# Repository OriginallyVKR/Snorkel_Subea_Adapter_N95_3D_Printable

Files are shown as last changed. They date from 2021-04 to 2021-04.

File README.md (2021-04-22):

# Snorkel_Subea_Adapter_N95_3D_Printable
This repo consists of the CAD designs of the adapter to convert a Decathlon - SUBEA snorkelling mask to be used as an N95 Mask for medical personnel. awe designed during the 

# Introduction 

<p>To prevent transmission of the novel SARS-CoV-2 virus among exposed health care workers (HCW), the WHO recommends the use of tight-fitting facepiece respirators such as the FFP2 or N95.1  However, global personal protective equipment (PPE) stockpiles are shrinking rapidly because of the elevated demand during the COVID-19 pandemic and since the capacity to expand PPE production is limited while supply chains are disrupted and counterfeit deliveries discovered, severe local shortages of trustworthy respirators are a reality.2-4  Possible deconfinement measures are likely to increase demand even further as indications to wear respirators become broader (i.e. semi-urgent surgery for affected COVID-19 patients)<sup>[<a href="https://www.researchgate.net/publication/341666605_Verification_of_two_Alternative_Do-it-yourself_Equipment_Respirators_Seal_as_COVID-19_Protection_VADERS-CoV_a_quality_assessment_pilot_study">source</a>]</sup>. 
  
  We aimed at mitigating the shortage of respirators with do-it-yourself Respirator (ADR) with components found in most hospitals - using a CPAP inline filter (using the appropriate filter - N-95, HEPA etc).
 
 On research we discovered that there was a snorkelling mask (sold by Decathlon - <a href="https://www.decathlon.in/p/8573237/easybreath-full-face-mask/adult-snorkeling-mask-easybreath-500-blue">ADULT SNORKELING MASK EASYBREATH 500</a>  )</p> which were readily available in most stores in our demographic (Bangalore, India), we then set out trying to design an adapter to connect the snorkelling mask to a CPAP inline filter. 
 
 # Design description
 
 <p> We started by exploring designs that were available in the open-source domain and landed a couple of adapters. We were fortunate enough to be able to source an FDM based 3D printer. The designs we found required support structures to be printed and had an average print time of 12 hours (15% infill) - the real challenge was once the print was done - post processing was a nightmare as the structure was such that it didnt allow us to clean up support material from the inner cavities. 
  
  We tried multiple orientations to reduce the support structures but were in no luck - the design by default was only available as STL files and gave us little flexibility to modify the wall thickness. The reason we wanted to alter the wall thickness was to increase our production rate, we wanted to be able to churn out 30 units in 3 days and the design didnt allow us to do this. Additionally, the adapter wasn't to operate at high pressure, we weren't looking at putting the adapter through any pressure higher than 14cmH2o (0.013bar or 1.199psi). 
  
  We soon realised that we had to start from scratch and brought in the  <a href="https://www.decathlon.in/p/8573237/easybreath-full-face-mask/adult-snorkeling-mask-easybreath-500-blue"> snorkelling</a> and the N95 CPAP filter, got the dimensions measured and designed the adapter. 
  
  With the newer design, we were able to print the adapter with no support (this was possible as we had redesigned the neck with lesser inclination, which allowed the printer to print subsequent layers with no underlying support as the layers weren't steep enough to warrant underlying support)
  
 PFB the drawings of the adapter: 
 
 Dimensions
 
 If you intend to modify the part, download the step file with the ".stp" extension to do so. Please note that we do not gurantee the performance if you undertake modifications ot the design. Please do reach out to us incase of any further questions.
 
 # Printer settings
 
 We used an FDM based printer with the following settings:

 * Material : PLA (polylactic acid) of 1.75mm red colour
 * Nozzle configuration : single nozzle 0.5mm
 * Infill : 15%
 * Speed : 100%
 * Supports : None
 * Z offset : None
 * Placement : placed flat with the wider mouth on the build plate (Refer image)
 
 Image from slicing software (we used Astro print <a href="https://cloud.astroprint.com/account/login"> Astroprint</a> as the slicer.
 
Screenshot from 2021-01-05 21-08-51
 
 The print time was close to 4.5/5 hours at the above-said configuration for a single unit, we then replicated this and generated a 5 unit configuration to print at scale. The results were as follows:
 
 Final_part_monoaxial

On connecting the CPAP inline N95 filter the results were as following:

Connected_final_monoaxial

We then printed about 5 as described earlier :

5_final__monoaxial

Images of doctors using it in on field:

Field_use_monoaxial

# Licenses 
  
<br /><span xmlns:dct="http://purl.org/dc/terms/" property="dct:title">Snorkel_Subea_Adapter_N95_3D_Printable</span> by <span xmlns:cc="http://creativecommons.org/ns#" property="cc:attributionName">Vishnu Ramakrishnan & Ateeb Hafeez</span> is licensed under a <a rel="license" href="http://creativecommons.org/licenses/by-nc/4.0/">Creative Commons Attribution-NonCommercial 4.0 International License</a>.<br />Based on a work at <a xmlns:dct="http://purl.org/dc/terms/" href="https://github.com/OriginallyVKR/Snorkel_Subea_Adapter_N95_3D_Printable" rel="dct:source">https://github.com/OriginallyVKR/Snorkel_Subea_Adapter_N95_3D_Printable</a>. 

# Contact us

For any queries additional you can write to us at vishnu.cats@gmail.com.

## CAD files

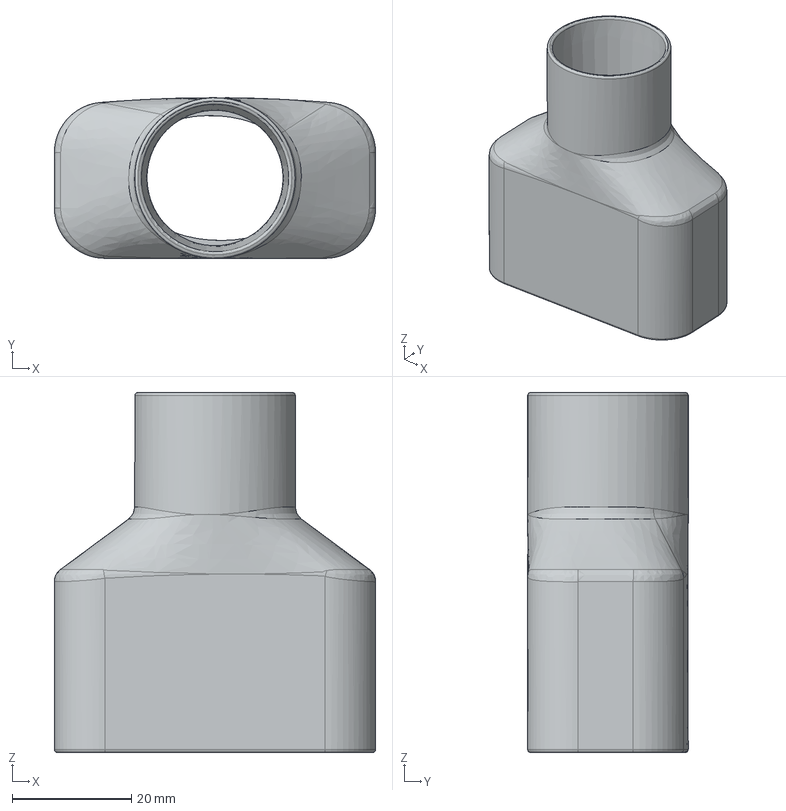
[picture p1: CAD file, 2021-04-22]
Monoaxial_Adapter_N95_CPAP.stp
54.0 x 27.0 x 60.5 mm

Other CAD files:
Monoaxial_Adapter_N95_CPAP.stl

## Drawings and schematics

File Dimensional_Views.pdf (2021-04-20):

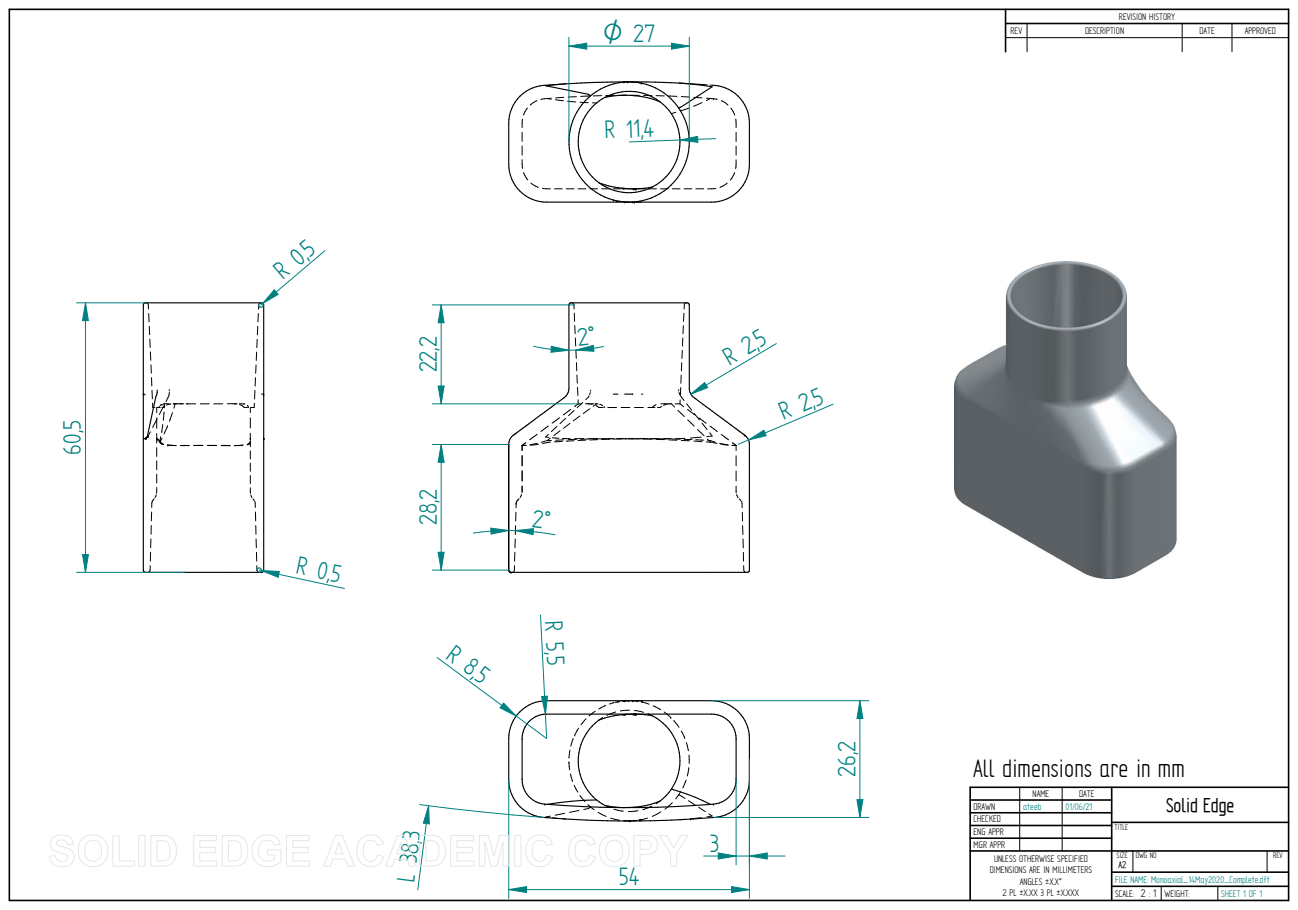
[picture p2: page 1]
TITLE; SCALE:; WEIGHT:; SHEET 1 OF 1

O 27 | REVISION HISTORY

REV | DESCRIPTION | DATE | APPROVED

All dimensions are in mm

NAME | DATE | Solid Edge

DRAWN | ateeb | 01/06/21
CHECKED
ENG APPR
MGR APPR
UNLESS OTHERWISE SPECIFIED DIMENSIONS ARE IN MILLIMETERS ANGLES ±X.X° 2 PL ±X.XX 3 PL ±X.XXX | SIZE A2 | DWG NO | REV

FILE NAME: Monoaxial_14May2020_Complete.dft
